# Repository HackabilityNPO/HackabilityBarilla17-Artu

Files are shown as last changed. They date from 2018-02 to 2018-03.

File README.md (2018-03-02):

# Artù - Hackability@Barilla

## What
Artù is a robotic exoskeleton designed for quadriplegic people that have limited movements in general and, therefore, many difficulties in the kitchen while cooking or eating. Artù helps these patients to hold and to use objects for cutting (all the knives) and hot cups, kettles and similar containers.

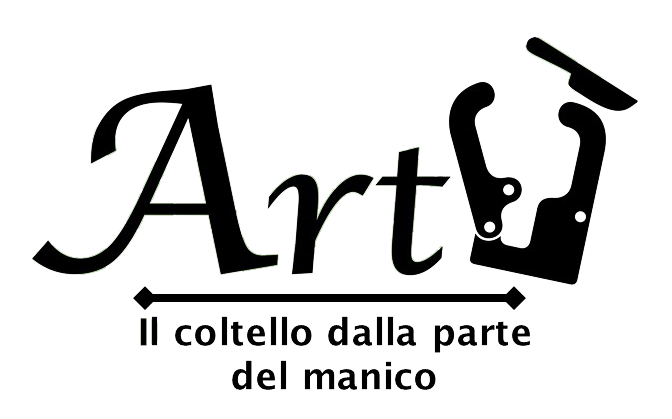
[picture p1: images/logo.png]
Hackability Logo


## Who (aka "Team Entusiasmo")

* Pietro Gemma
* Enrico Bassi
* Cristiana Giordano
* Emanuele Goldoni
* Luisa Carnevale Baraglia
* Nadia Crivelli
* Giuseppa Cafueri

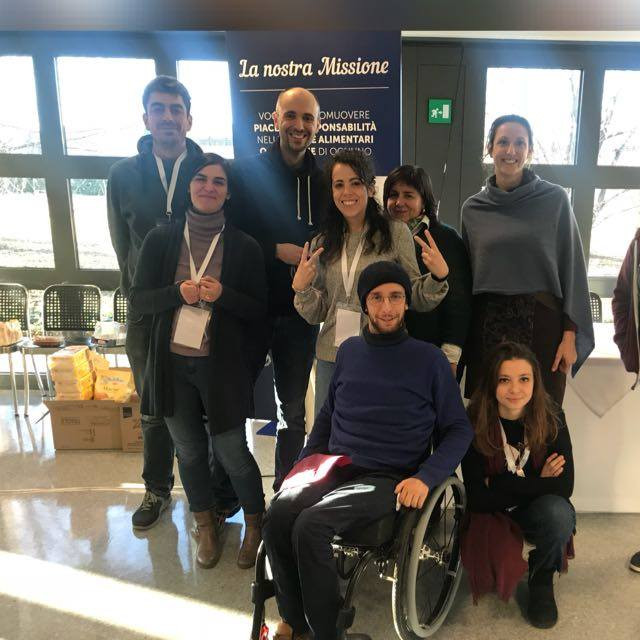
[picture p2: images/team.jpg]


## Why / When / Where

Artù was born around the needs of Pietro, our friend who lost the use of arms and legs due to an accident.

The whole team created Artù during [Hackability@Barilla](http://www.hackability.it/hackabilitybarilla/). The development took about one month, from January 20, 2018 to February 23, 2018.

The original idea was conceived at the Barilla Headquarters, Parma; the actual design, development and testing was carried out in Mantova (LTO Mantova) and Milano (Opendot).

## How

### BOM - Bill of Materials

* 1x DC 12V reversible high-torque worm gear box reduction electric motor
* 2x big push-buttons for controlling the movement
* 1x switch for turning on-off the system
* 1x 2600lithium-battery bank which powers all the system 
* 1x Arduino Nano
* 1x L9110S-based H-bridge motor driver controller 
* 1x XL6009-based DC DC step-up
* a bunch of screws, cables and connectors
* tens of meters of PLA filament

### The exoskeleton

Artù has a lightweight exoskeleton molded specifically on the shape of Pietro's forearm.
The first prototype was made with modeling paste and foam core. A second prototype was made of polyethylene, again molded on the shape of Pietro's forearm.
Then, we designed a flattened version of exoskeleton in CAD and we made it lightweight using a honeycomb-like structure. The exoskeleton can be easily and quickly printed in 3D and hot bended around the arm.

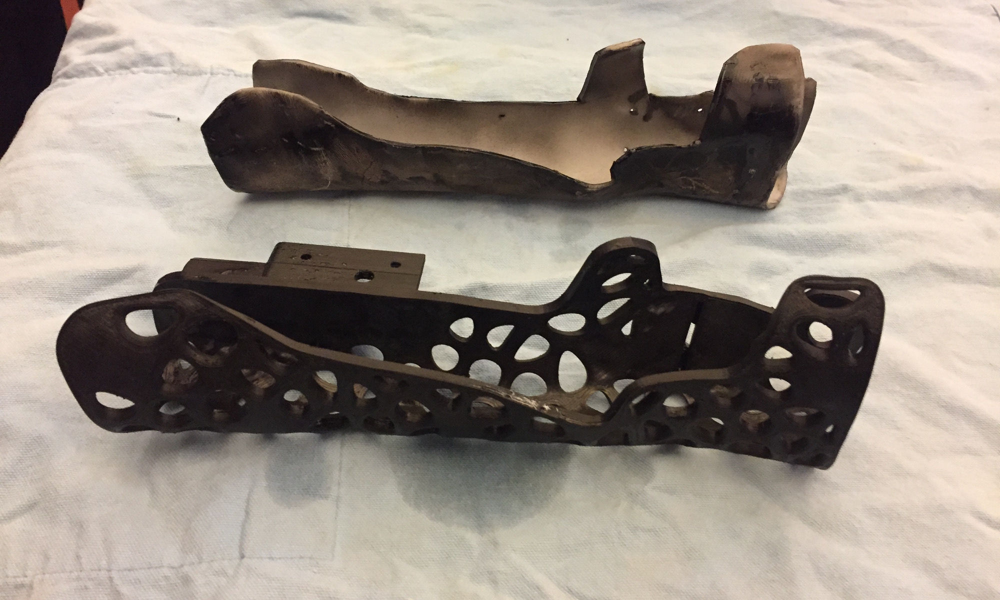
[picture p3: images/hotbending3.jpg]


The exoskeleton has a movable plier to hold the objects and which can be rotated at different angles.
The bottom part of the plier is provided a straight bevel gear. This gear is coupled with a similar parallel gear near the palm of the exoskeleton. The gears have 12 teeth, so 12 possible rotating positions (30 degrees each) are allowed. In each of these positions, the two gears fit perfectly and are in a minimum-energy position. Using a thin steel thread, we can pull the plier towards the palm, keeping them locked in the desired position.

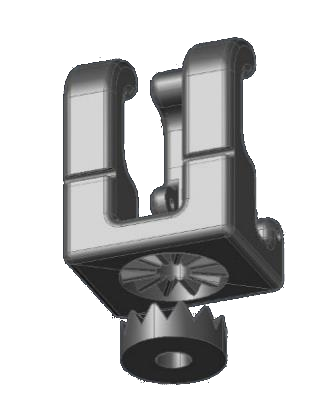
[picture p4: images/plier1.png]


### The motorized plier

The exoskeleton mounts a DC 12V reversible high-torque electric motor. We used a 5rpm motor - honestly, its quite precise but slow (faster configurations are available as well). 

The motor is connected to a motor driver controller - the driver is powered by a step up, which increases the 5V voltage of the power bank USB output to 12V. The driver is also controlled by two pins of the Arduino Nano board. This board, which is too powered by the power bank, is also connected to the two push-buttons. The input pins are configured in pullup mode - the buttons short-circuits the input to ground when they are pressed.

The code running on the Arduino board is quite simple - it reads the inputs and moves the motor accordingly. The values are read every 100 ms - for security reasons, you need to keep the button pressed to confirm you want to move the motor (otherwise, it stays off).

The switch physically disconnects the power source from the circuit (best way to save power). A USB-male terminated cable allows to recharge the power bank using a standard recharger (or even the USB port of a computer).

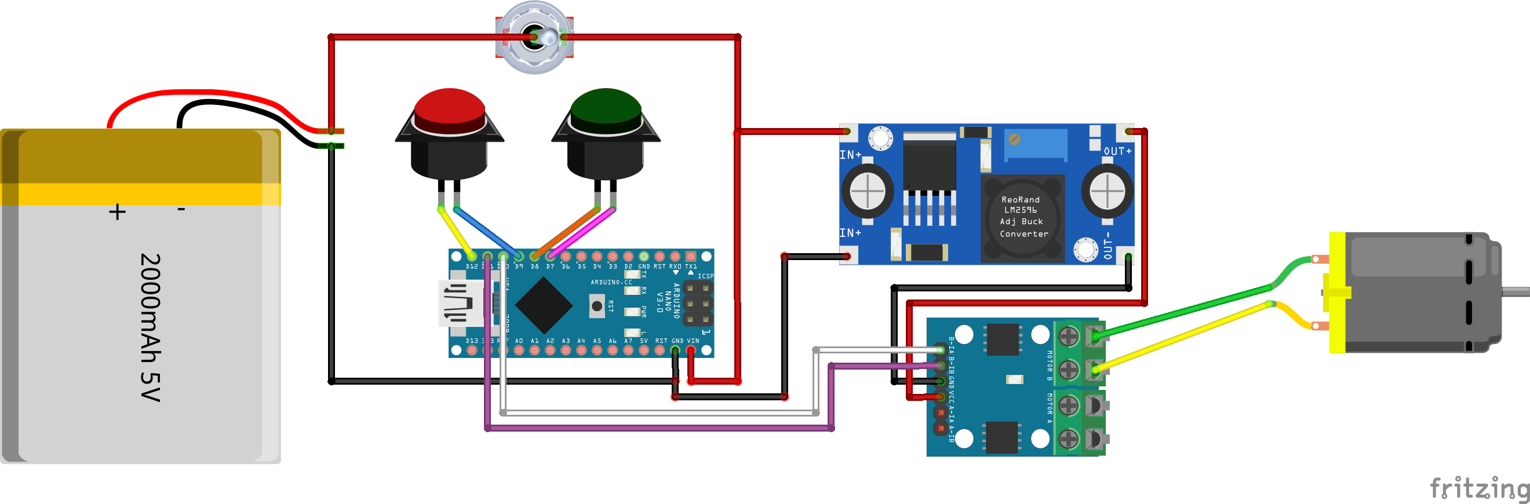
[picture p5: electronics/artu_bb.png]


We were able to run the motor also powering it at 5V from the USB, without using the step up - the rotation was a bit slower but still usable.

### The assembled tool

As you see below, the plier is connected to the motor, which moves pull a steel thread, thus moving the finger and tightening the plier. The motor is connected to the external box (bottom right in the photo), which contains the USB-rechargeable power bank and two buttons on the top of the box for moving backward or forward the motor head.

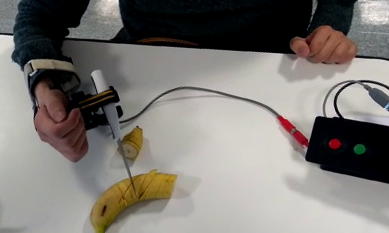
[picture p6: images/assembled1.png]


## The Repository is organized as following

 - `README.md`. General information about the project.
 - `mechanics/`. digital files describing mechanics components.
 - `electronics/`.  digital files describing electronics components used.
 - `software/`. software developed.
 - `images/`. images, photos of the work, etc.
 - `videos/`. videos of the project in action.

## License

All the material is available under the terms of the CC BY-SA 4.0 license (Creative Commons Attribution-ShareAlike 4.0 International License)

## In action...

A *[video](https://youtu.be/Hmfroie_xvs)* is worth a thousand words!

So long, and thanks for all the bananas :-)

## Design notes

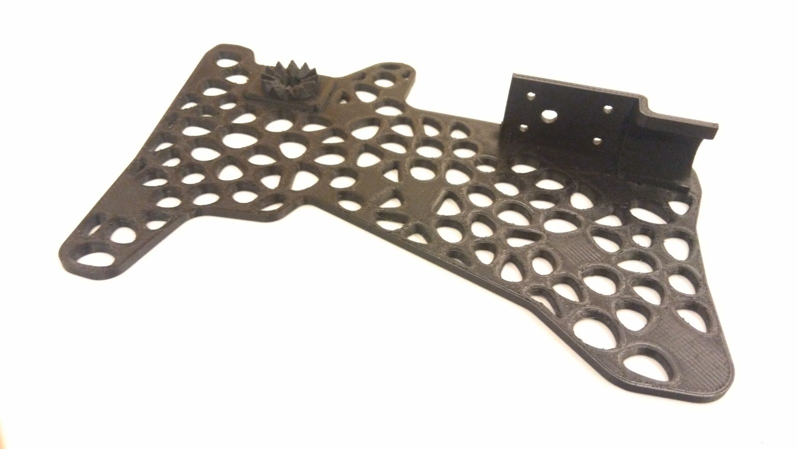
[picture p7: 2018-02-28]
images/exoskeleton1.jpeg

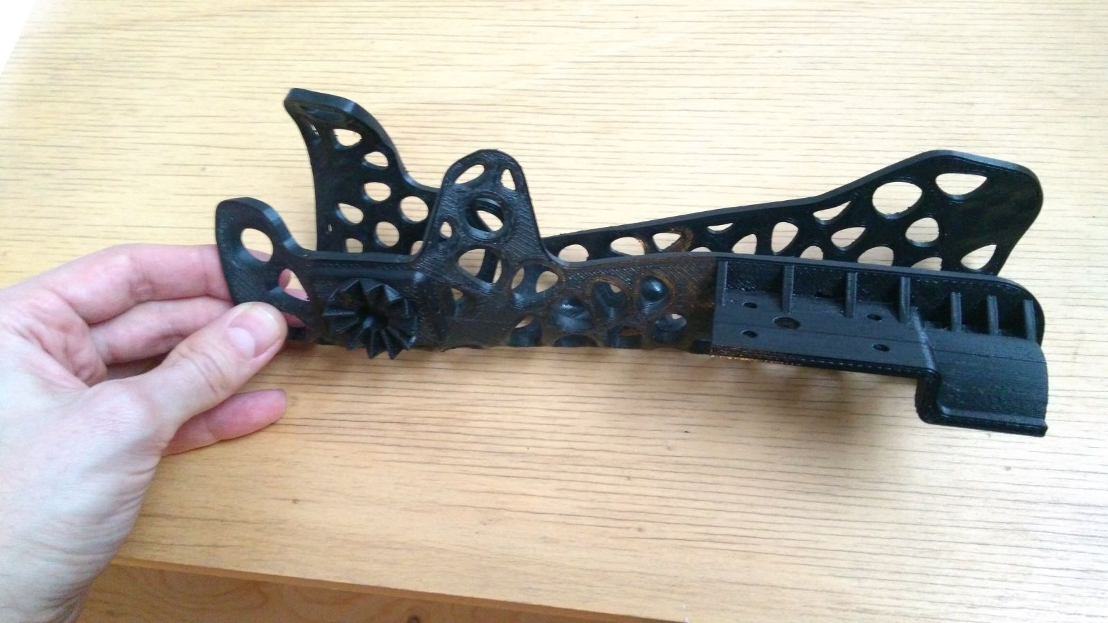
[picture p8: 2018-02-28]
images/exoskeleton2.jpeg

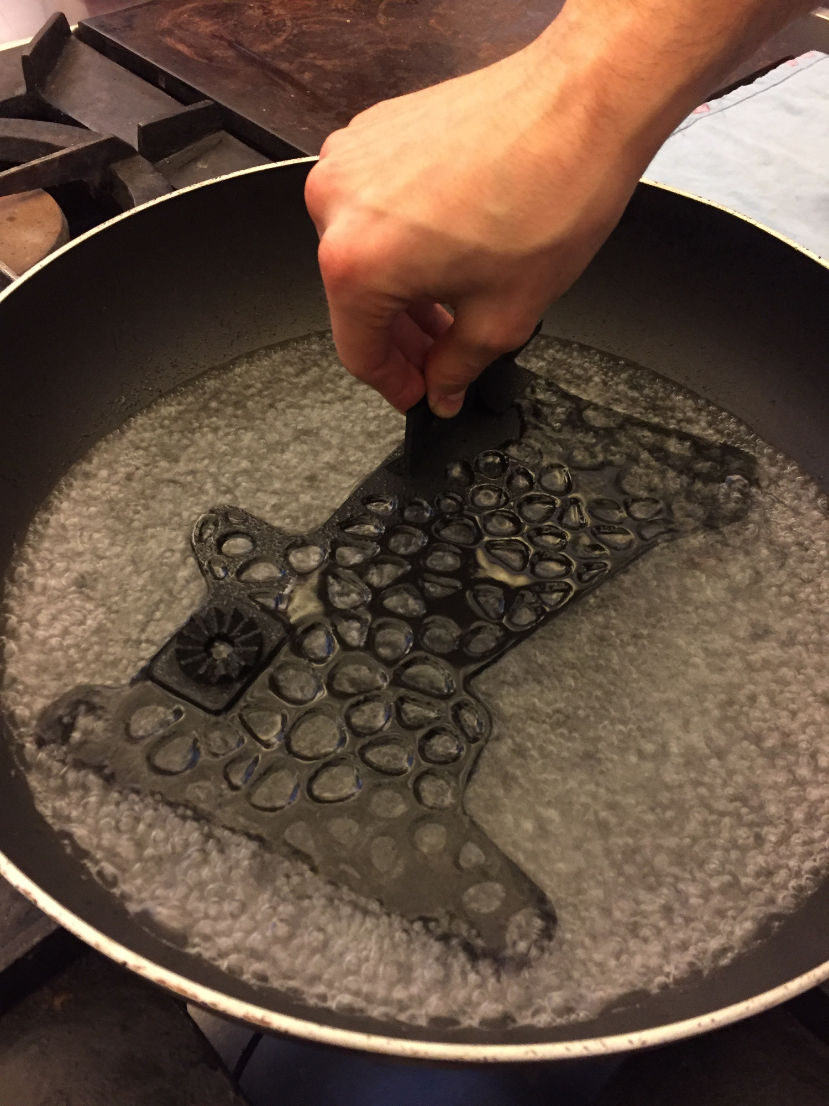
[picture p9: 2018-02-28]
images/hotbending1.jpg

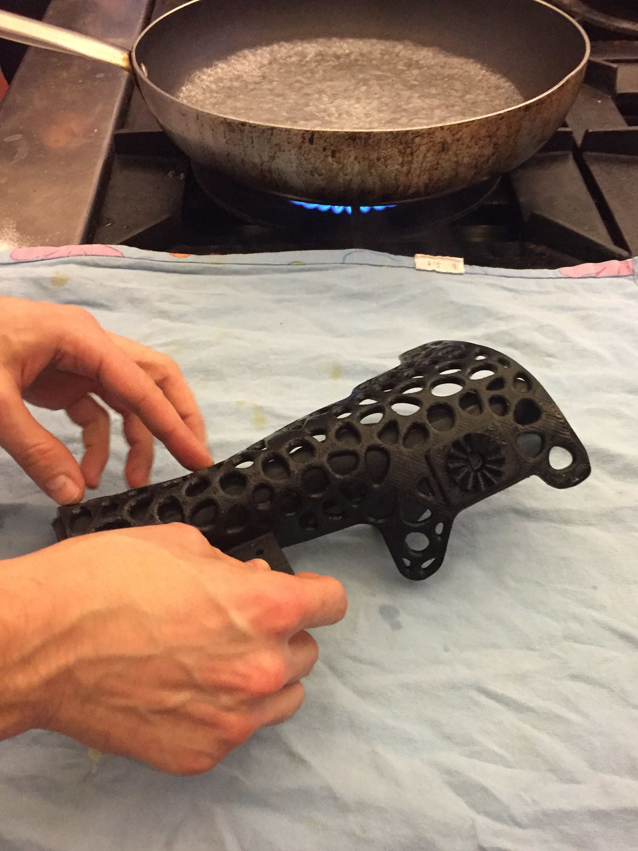
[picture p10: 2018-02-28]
images/hotbending2.jpg

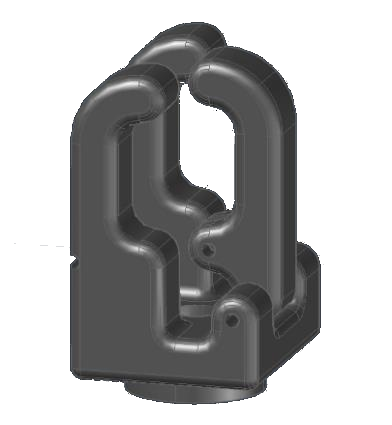
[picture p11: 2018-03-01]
images/plier2.png

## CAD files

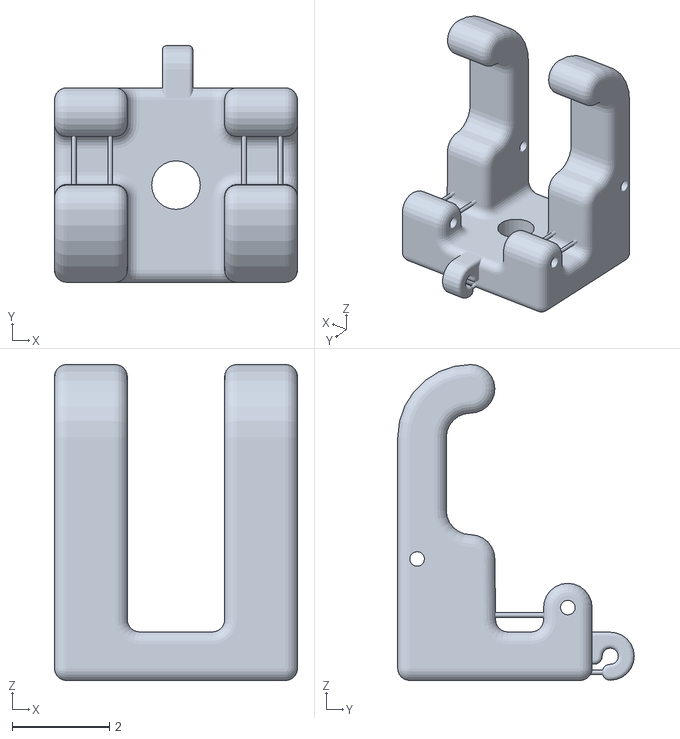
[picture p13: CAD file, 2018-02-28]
mechanics/main_plier.stl
5.00 x 4.87 x 6.50

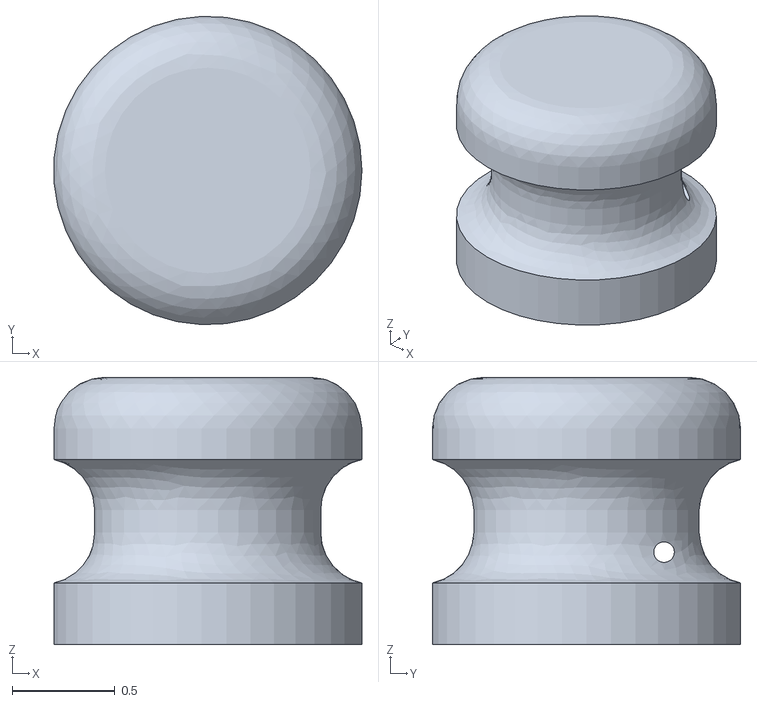
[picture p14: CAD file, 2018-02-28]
mechanics/D-shaped_motor_cap.stl
1.50 x 1.50 x 1.30

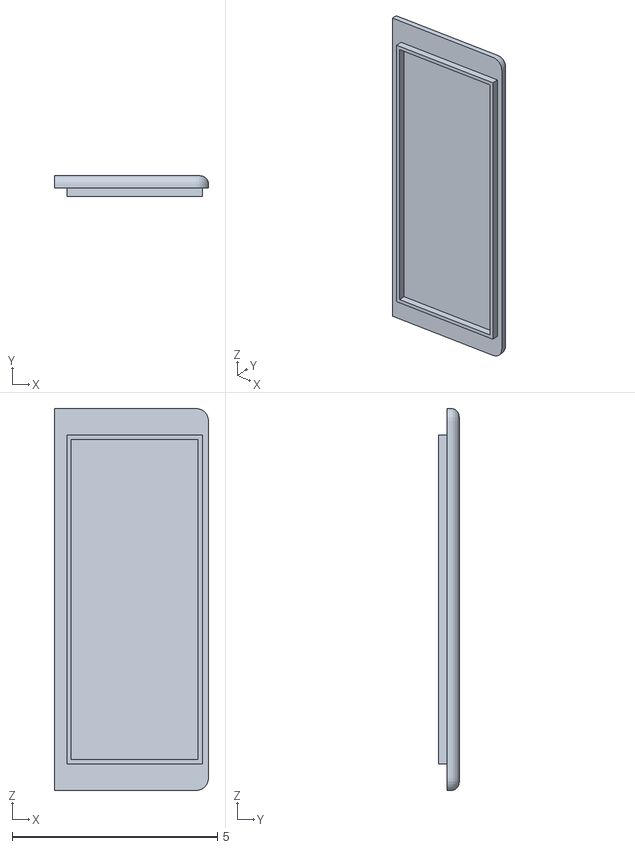
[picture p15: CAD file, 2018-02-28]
mechanics/motor_box_cover.stl
3.75 x 0.5 x 9.30

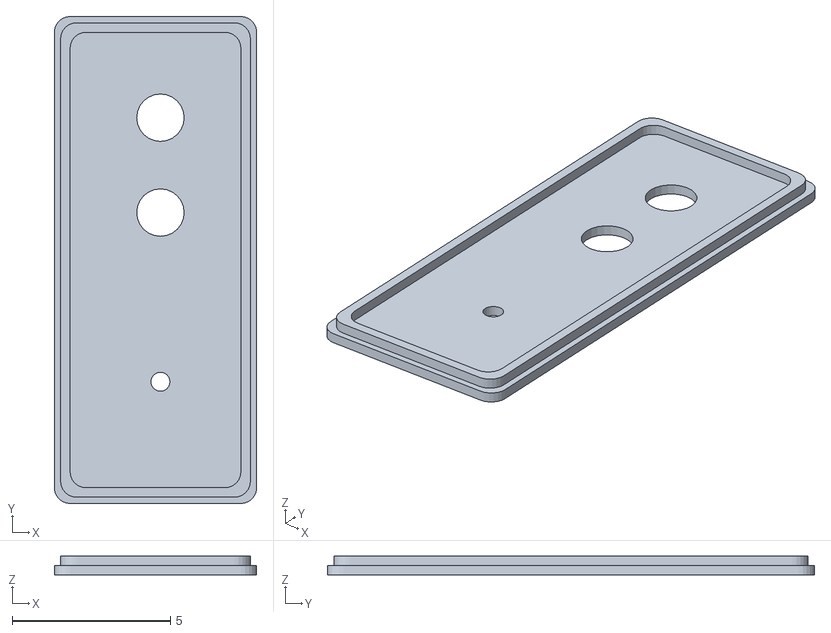
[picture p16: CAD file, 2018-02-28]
mechanics/control_box_cover.stl
6.40 x 15.4 x 0.6

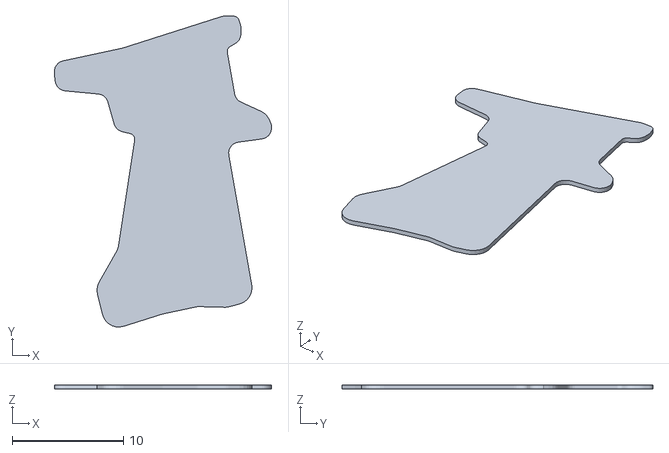
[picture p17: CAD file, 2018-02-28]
mechanics/raw_exoskeleton.stl
19.6 x 28.0 x 0.4

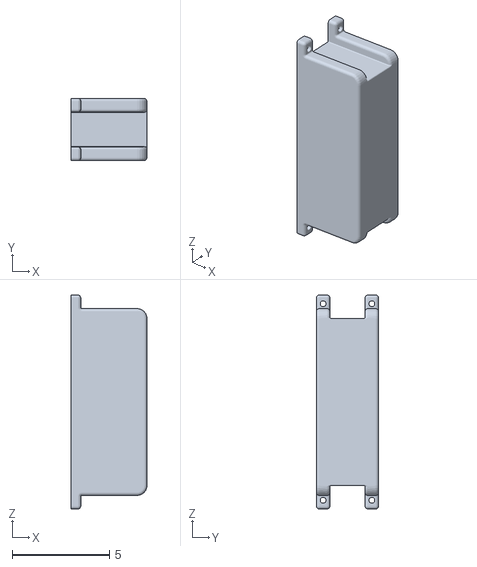
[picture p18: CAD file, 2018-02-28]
mechanics/motor_box.stl
3.90 x 3.20 x 11.0

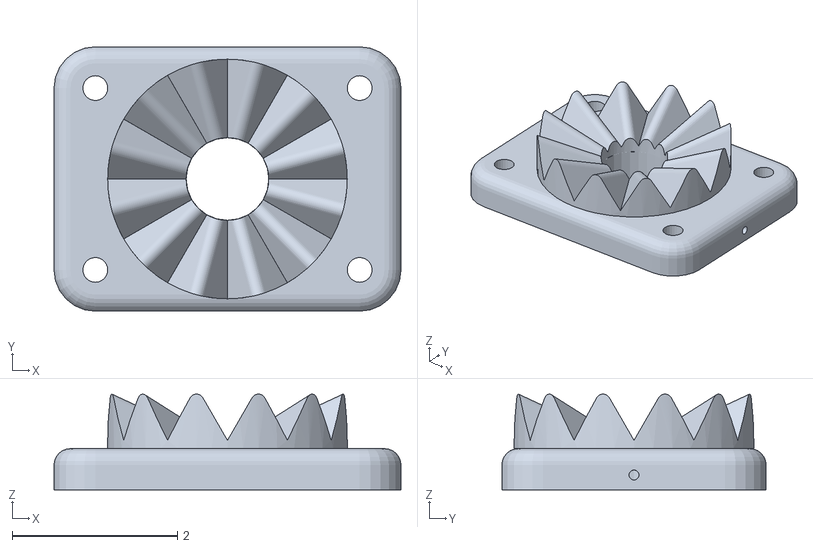
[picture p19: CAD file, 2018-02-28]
mechanics/anchor_plate_with_bevel_gear.stl
4.20 x 3.20 x 1.16

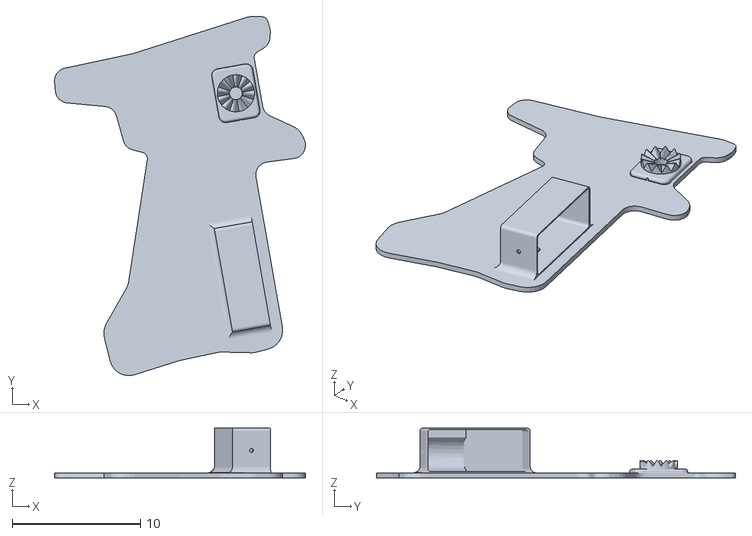
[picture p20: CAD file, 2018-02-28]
mechanics/exoskeleton_v1.stl
19.6 x 28.0 x 3.90

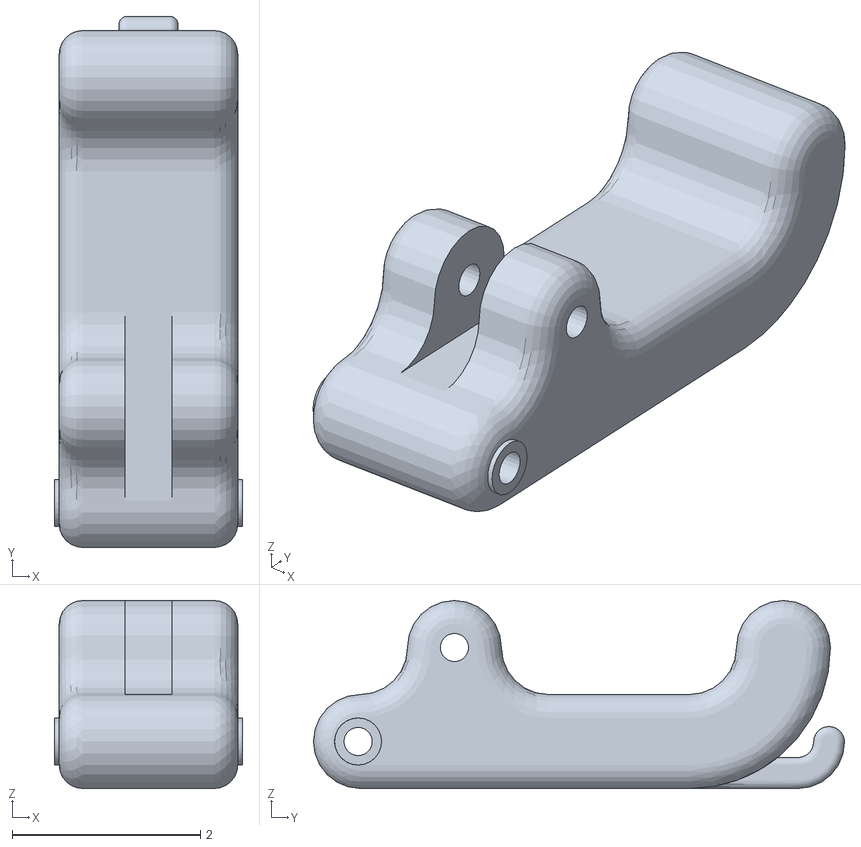
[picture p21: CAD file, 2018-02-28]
mechanics/movable_finger.stl
2.00 x 5.65 x 2.00

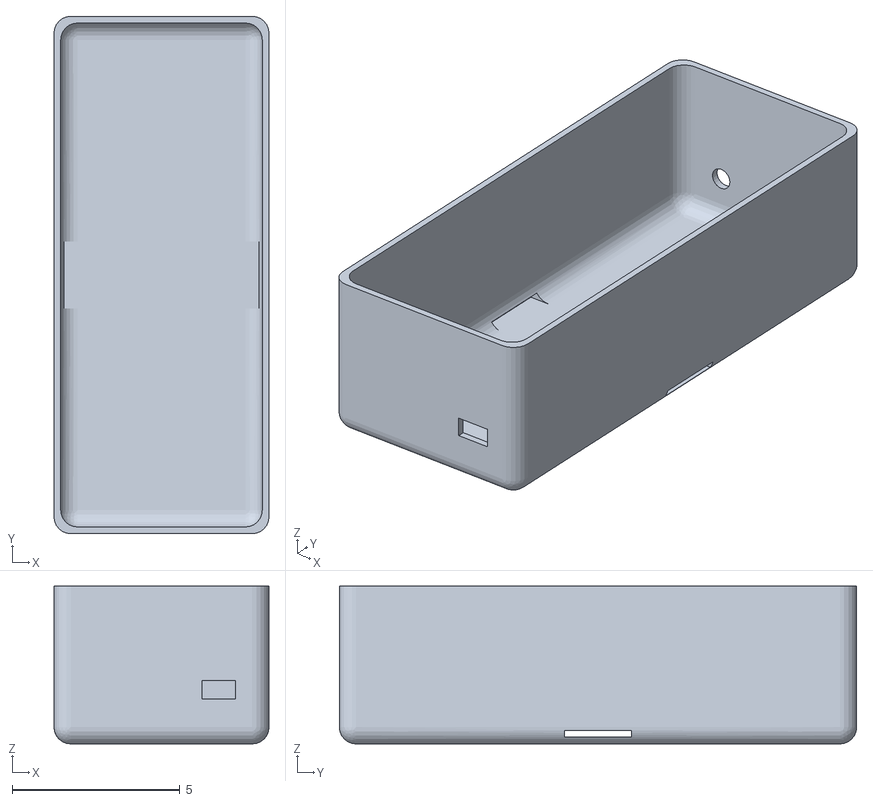
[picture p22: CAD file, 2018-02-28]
mechanics/control_box.stl
6.40 x 15.4 x 4.70

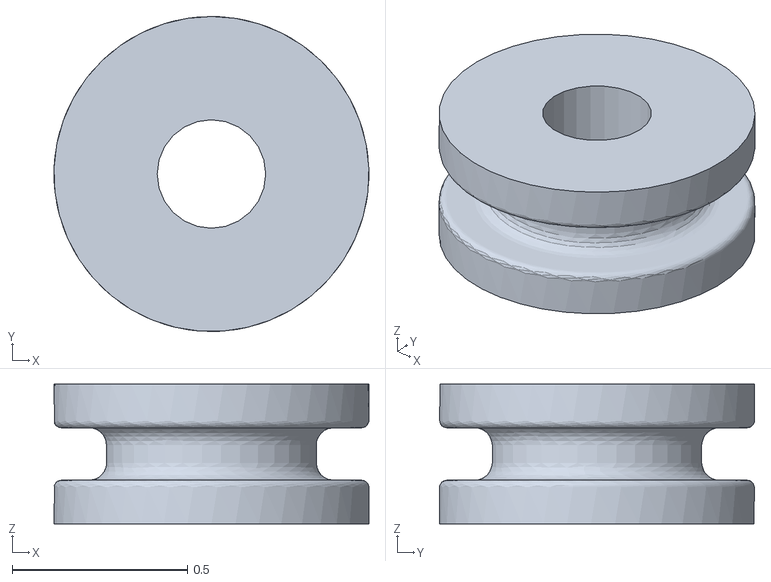
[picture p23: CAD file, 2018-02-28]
mechanics/flat_washer.stl
0.9 x 0.9 x 0.4

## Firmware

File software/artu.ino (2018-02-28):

#define BUTTON_FW 8
#define BUTTON_BW 9
#define MOTOR_B_DIR 10  //L9110_B_IA
#define MOTOR_B_PWM 11  //L9110_B_IB
#define GDN_PIN1 12
#define GDN_PIN2 7
#define PWM_FW 150
#define PWM_BW 75

void setup()
{
  pinMode(BUTTON_FW, INPUT_PULLUP);
  pinMode(BUTTON_BW, INPUT_PULLUP);
  pinMode(MOTOR_B_DIR, OUTPUT);
  pinMode(MOTOR_B_PWM, OUTPUT);
  pinMode(GDN_PIN1, OUTPUT);
  digitalWrite(GDN_PIN1, LOW);
  pinMode(GDN_PIN2, OUTPUT);
  digitalWrite(GDN_PIN2, LOW);
}

void loop()
{
  delay(5);
  int btn_fw = digitalRead(BUTTON_FW);
  delay(5);
  int btn_bw = digitalRead(BUTTON_BW);
  delay(5);
  
  if (btn_bw == LOW) {
    // move backward
    digitalWrite(MOTOR_B_DIR, HIGH);
    analogWrite(MOTOR_B_PWM, PWM_BW);
    digitalWrite(13, HIGH);
  } else if (btn_fw == LOW) {
    // move forward
    digitalWrite(MOTOR_B_DIR, LOW);
    analogWrite(MOTOR_B_PWM, PWM_FW);
    digitalWrite(13, HIGH);
  } else {
    // turn motor off
    digitalWrite(MOTOR_B_DIR, LOW);
    analogWrite(MOTOR_B_PWM, 0);
    digitalWrite(13, LOW);
  }
  delay(100);
}

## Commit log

2018-02-28 files - part1
    [anchor_plate_with_bevel_gear.stl, control_box.stl, control_box_cover.stl, exoskeleton_v1.stl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]
2018-03-02 issue #1 - remove sample description files
